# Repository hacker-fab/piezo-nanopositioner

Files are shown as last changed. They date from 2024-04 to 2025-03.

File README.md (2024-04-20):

# piezo-nanopositioner

To install the ESP-IDF you should follow this guide for [Linux and macOS](https://docs.espressif.com/projects/esp-idf/en/v5.2.1/esp32s3/get-started/linux-macos-setup.html) and [Windows](https://docs.espressif.com/projects/esp-idf/en/v5.2.1/esp32s3/get-started/windows-setup.html). Once you have the ESP-IDF installed you will need to run the `export.sh` file located in `esp/esp-idf/export.sh` inside the `esp` folder you setup. Once you have setup ESP-IDF for your current terminal session, you can now run `idf.py build` to compile the code or `idf.py -p {serial port the device is connected to} flash`.

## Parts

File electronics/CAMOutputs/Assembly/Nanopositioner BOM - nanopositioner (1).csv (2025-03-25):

Qty | Designator | MPN | Description | Value | Footprint
1 | SV2 |  | PIN HEADER |  | MA08-1
1 | SV1 |  | PIN HEADER |  | MA10-1
3 | C5, C9, C10 | GRM155R71H104KE14D | CAPACITOR, European symbol | 100n | C0402
1 | C15 | CGA3E2X7R1H104K080AA | CAPACITOR, European symbol | 100n | C0603
1 | C16 | KGM21NR71E104KT | CAPACITOR, European symbol | 100n | C0603
4 | R5, R7, R8, R9 | ERA-2AEB103X | RESISTOR, European symbol | 10k | R0402
1 | C3 | GCM155R71H103KA55D | CAPACITOR, European symbol | 10n | C0402
1 | C13 | GRM033R70J103KA01D | CAPACITOR, European symbol | 10n | C0402
1 | R1 | CRCW04021K91FKED | RESISTOR, European symbol | 1k91 | R0402
1 | C17 | EMK107B7105KA-T | CAPACITOR, European symbol | 1u | C0402
4 | C2, C6, C7, C8 | GRM155R61E105MA12D | CAPACITOR, European symbol | 1u | C0402
2 | C1, C4 | CL10A226MP8NUNE | CAPACITOR, European symbol | 22u | C0603
1 | C11 | GRM155R71A273KA01D | CAPACITOR, European symbol | 27n | C0402
1 | R13 | CRCW04022K49FKED | RESISTOR, European symbol | 2k49 | R0402
1 | C20 | GRM21BR71A225KA01L | CAPACITOR, European symbol | 2u2 | C0805
1 | L1 | SDR1307-2R7ML |  | 2u7, 8m | IND_BOURNS_SDR1307
1 | R6 | CRCW040257K6FKED | RESISTOR, European symbol | 57k6 | R0402
5 | R2, R3, R10, R11, R12 | ERA-2AEB512X | RESISTOR, European symbol | 5k1 | R0402
1 | C12 | GRM1555C1H5R6CA01D | CAPACITOR, European symbol | 5p6 | C0402
1 | J1 | 12402012E212A | WR-COM USB 2.0 Type C Plug Vertical SMT | 629722000214 | 629722000214
3 | C14, C18, C19 | C3216X5R1H685K160AB | CAPACITOR, European symbol | 6u8 | C1206
2 | R4, R14 | CRCW04029K76FKED | RESISTOR, European symbol | 9k76 | R0402
1 | D1 | B240A-13-F | Diode Schottky 40V 2A Surface Mount SMA | B240A-13-F | DIOM5226X230N
1 | U3 | DAC80504RTET |  | DAC80504RTER | RTE16_TEX
1 | U4 | ESP32-S3-WROOM-1-N4 | Check availability Check availability | ESP32-S3-WROOM-1-N4R8 | XCVR_ESP32S3WROOM1N8R8
1 | U5 | LM5157RTER |  | LM5157RTER | QFN_57RTER_TEX
1 | I1 | OPA4209AIPW |  | OPA4209AIPW | PW14
3 | TP2, TP4, TP10 |  | TEST PIN | PTR1PAD1-13 | P1-13
1 | U1 | TPS73633DBVR |  | TPS73633DBVR | DBV5
1 | U2 | USBLC6-2SC6 |  | USBLC6-2SC6 | SOT23-6L_STM

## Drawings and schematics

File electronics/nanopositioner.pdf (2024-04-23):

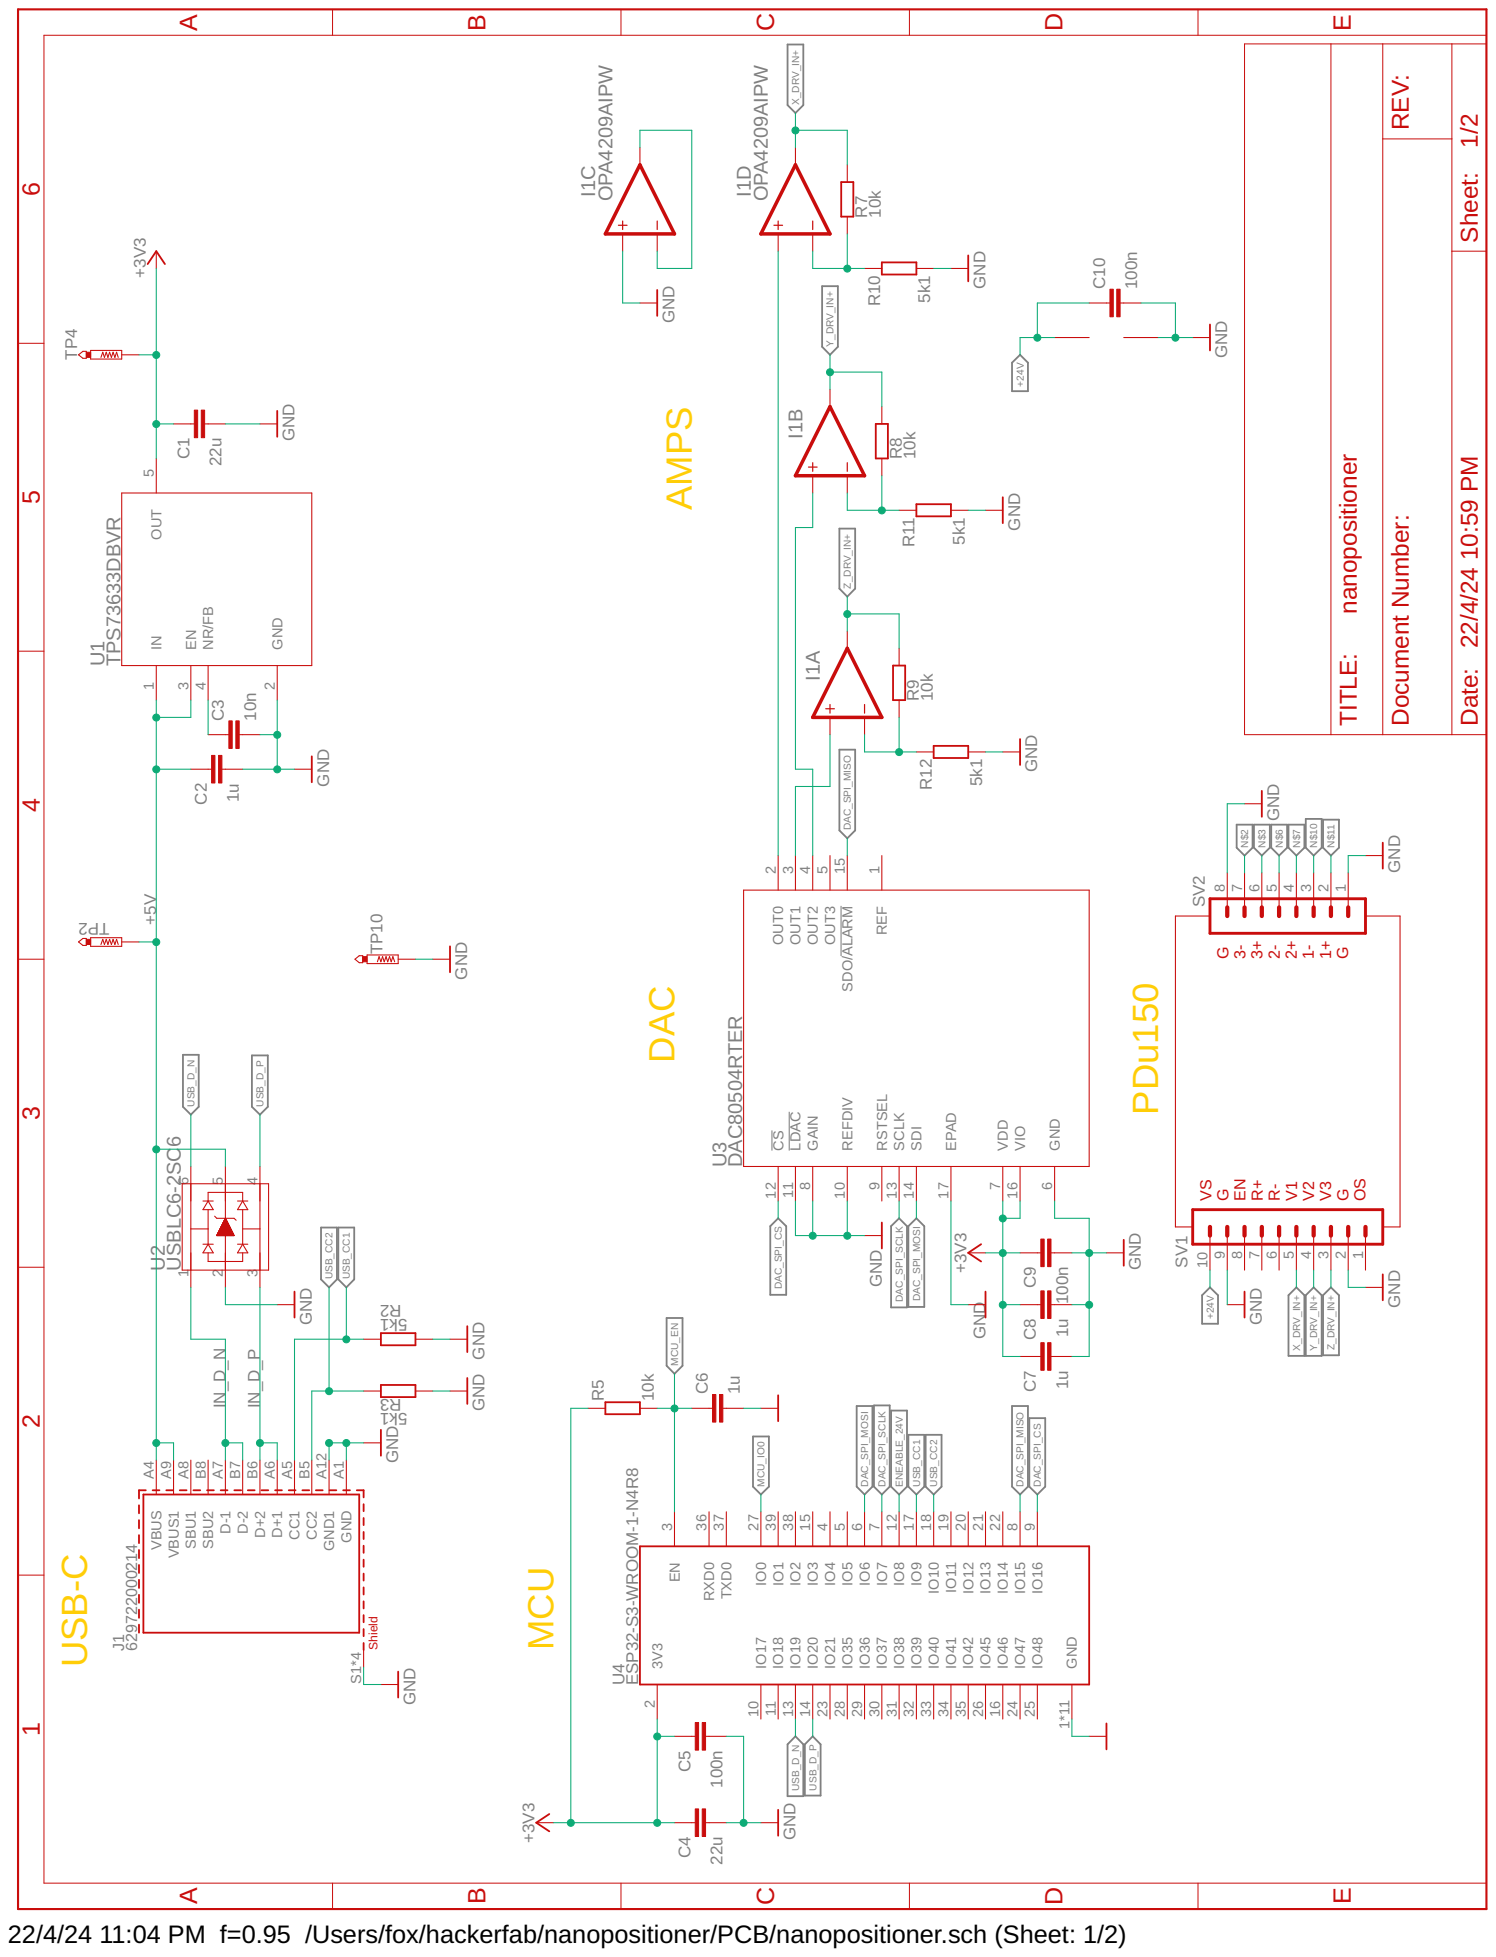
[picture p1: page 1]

GND GND

22/4/24 11:04 PM f=0.95 /Users/fox/hackerfab/nanopositioner/PCB/nanopositioner.sch (Sheet: 1/2)

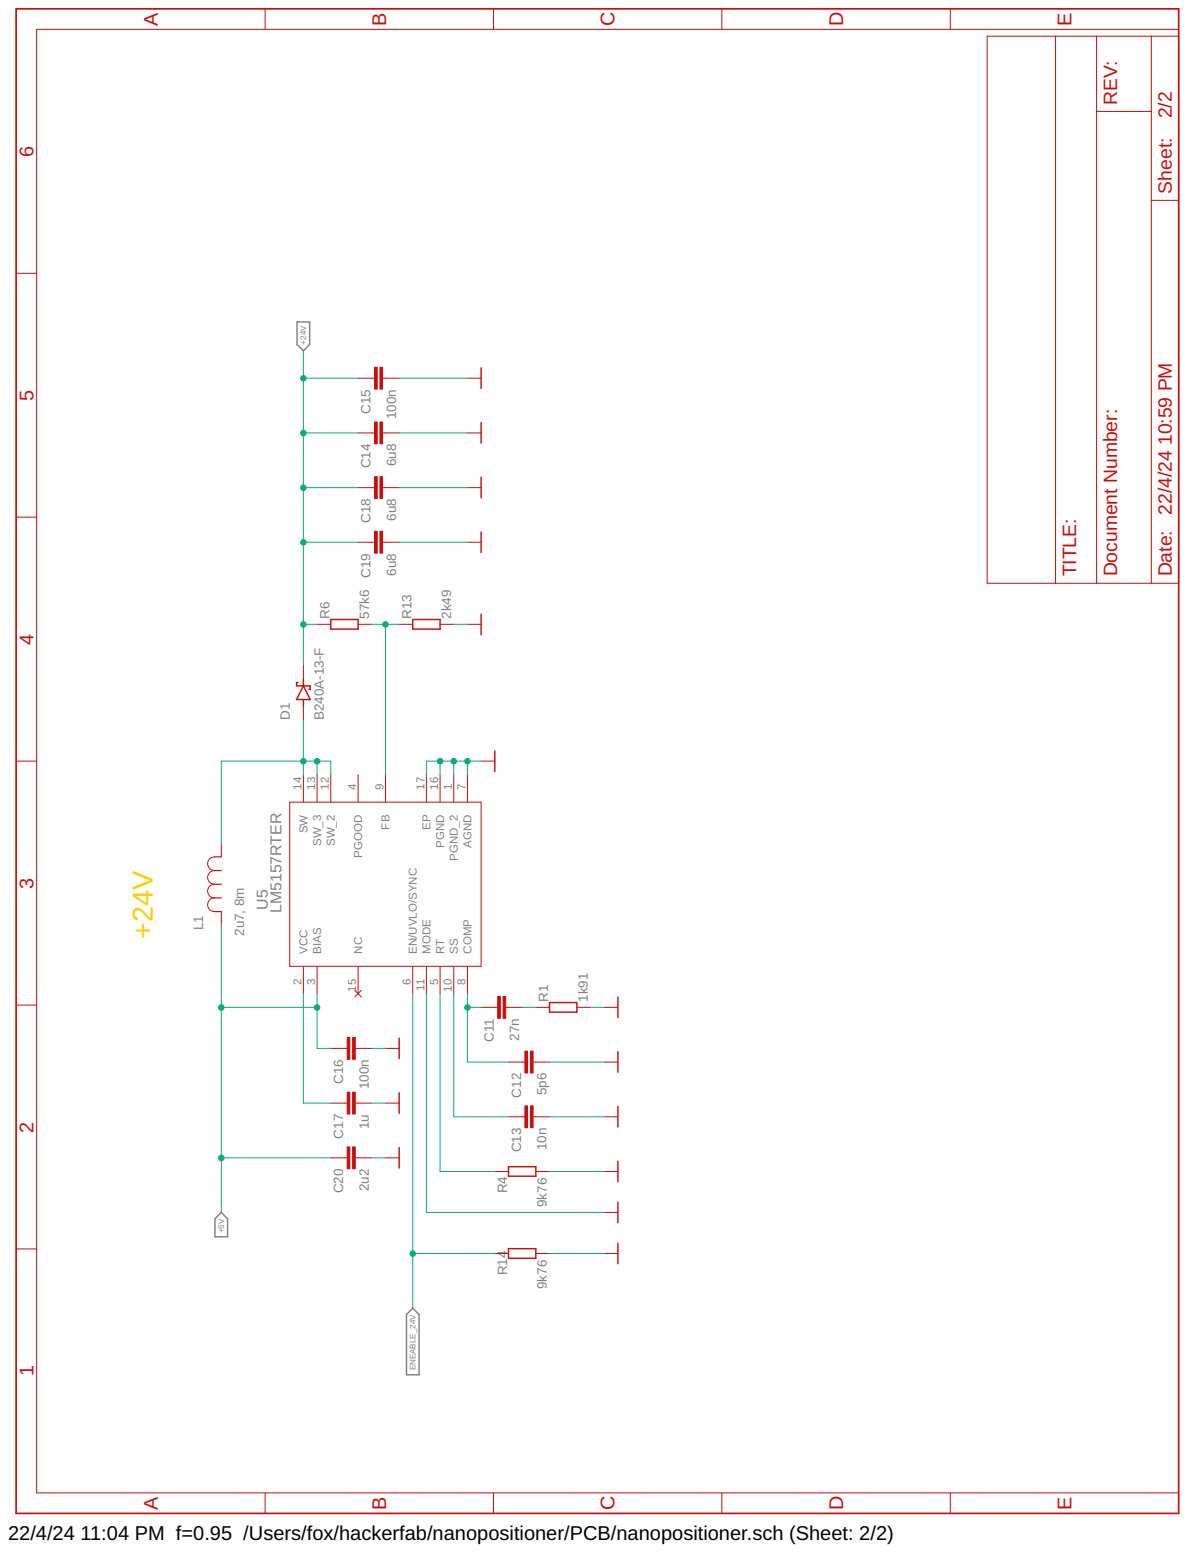
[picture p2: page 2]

22/4/24 11:04 PM f=0.95 /Users/fox/hackerfab/nanopositioner/PCB/nanopositioner.sch (Sheet: 2/2)

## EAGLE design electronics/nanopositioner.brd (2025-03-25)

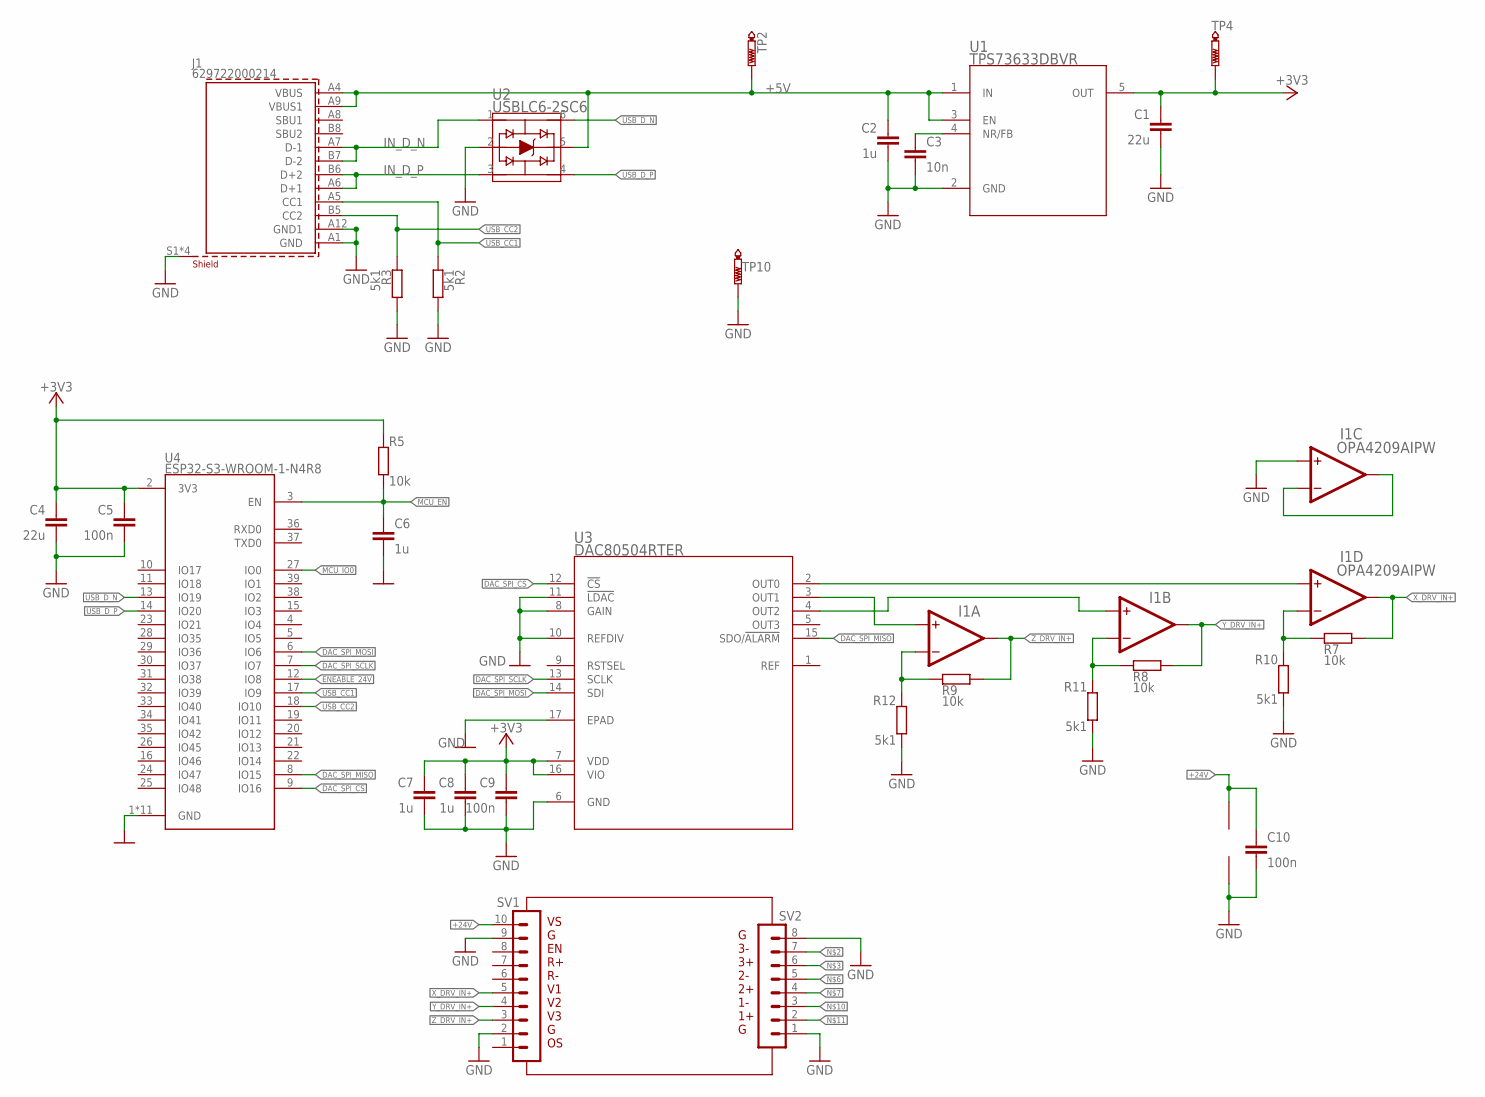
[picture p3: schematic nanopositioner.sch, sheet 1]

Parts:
C1, C4: 22u; C0603; MPN CL10A226MP8NUNE
C2, C6, C7, C8: 1u; C0402; MPN GRM155R61E105MA12D
C3: 10n; C0402; MPN GCM155R71H103KA55D
C5, C9, C10: 100n; C0402; MPN GRM155R71H104KE14D
I1: OPA4209AIPW; PW14; MPN OPA4209AIPW
J1: 629722000214; MPN 12402012E212A
R2, R3, R10, R11, R12: 5k1; R0402; MPN ERA-2AEB512X
R5, R7, R8, R9: 10k; R0402; MPN ERA-2AEB103X
SV1: MA10-1
SV2: MA08-1
TP2, TP4, TP10: PTR1PAD1-13; P1-13
U1: TPS73633DBVR; DBV5; MPN TPS73633DBVR
U2: USBLC6-2SC6; SOT23-6L_STM; MPN USBLC6-2SC6
U3: DAC80504RTER; RTE16_TEX; MPN DAC80504RTET
U4: ESP32-S3-WROOM-1-N4R8; XCVR_ESP32S3WROOM1N8R8; MPN ESP32-S3-WROOM-1-N4

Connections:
+3V3: C1.1, C4.1, C5.1, C7.1, C8.1, C9.1, R5.1, TP4.TP, U1.5 (OUT), U3.7 (VDD), U3.16 (VIO), U4.2 (3V3)
+5V: C2.2, J1.A4 (VBUS), J1.A9 (VBUS1), TP2.TP, U1.1 (IN), U1.3 (EN), U2.5; also elsewhere on the board
+24V: C10.1, I1.4, SV1.10; also elsewhere on the board
DAC_SPI_CS: U3.12 (!CS), U4.9 (IO16)
DAC_SPI_MISO: U3.15 (SDO/!ALARM), U4.8 (IO15)
DAC_SPI_MOSI: U3.14 (SDI), U4.6 (IO6)
DAC_SPI_SCLK: U3.13 (SCLK), U4.7 (IO7)
ENEABLE_24V: U4.12 (IO8); also elsewhere on the board
GND: C1.2, C2.1, C3.2, C4.2, C5.2, C6.1, C7.2, C8.2, C9.2, C10.2, I1.10 (INA+), I1.11, J1.A1 (GND), J1.A12 (GND1), J1.S1 (SHIELD), J1.S2 (SHIELD), J1.S3 (SHIELD), J1.S4 (SHIELD), R2.1, R3.2, R10.2, R11.2, R12.2, SV1.2, SV1.9, SV2.1, SV2.8, TP10.TP, U1.2 (GND), U2.2, U3.6 (GND), U3.8 (GAIN), U3.10 (REFDIV), U3.11 (!LDAC), U3.17 (EPAD), U4.1 (GND), U4.40 (GND), U4.41_1 (GND), U4.41_2 (GND), U4.41_3 (GND), U4.41_4 (GND), U4.41_5 (GND), U4.41_6 (GND), U4.41_7 (GND), U4.41_8 (GND), U4.41_9 (GND); also elsewhere on the board
IN_D_N: J1.A7 (D-1), J1.B7 (D-2), U2.1
IN_D_P: J1.A6 (D+1), J1.B6 (D+2), U2.3
MCU_EN: C6.2, R5.2, U4.3 (EN)
MCU_IO0: U4.27 (IO0)
unnamed: I1.13 (INA-), R7.1, R10.1
unnamed: C3.1, U1.4 (NR/FB)
unnamed: I1.3 (INA+), U3.3 (OUT1)
unnamed: I1.6 (INA-), R8.1, R11.1
unnamed: I1.5 (INA+), U3.4 (OUT2)
unnamed: I1.2 (INA-), R9.1, R12.1
unnamed: I1.12 (INA+), U3.2 (OUT0)
unnamed: I1.8 (OUTA), I1.9 (INA-)
USB_CC1: J1.A5 (CC1), R2.2, U4.17 (IO9)
USB_CC2: J1.B5 (CC2), R3.1, U4.18 (IO10)
USB_D_N: U2.6, U4.13 (IO19)
USB_D_P: U2.4, U4.14 (IO20)
X_DRV_IN+: I1.14 (OUTA), R7.2, SV1.5
Y_DRV_IN+: I1.7 (OUTA), R8.2, SV1.4
Z_DRV_IN+: I1.1 (OUTA), R9.2, SV1.3

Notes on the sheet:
VS G EN R+ R- V1 V2 V3 G OS
G 3- 3+ 2- 2+ 1- 1+ G

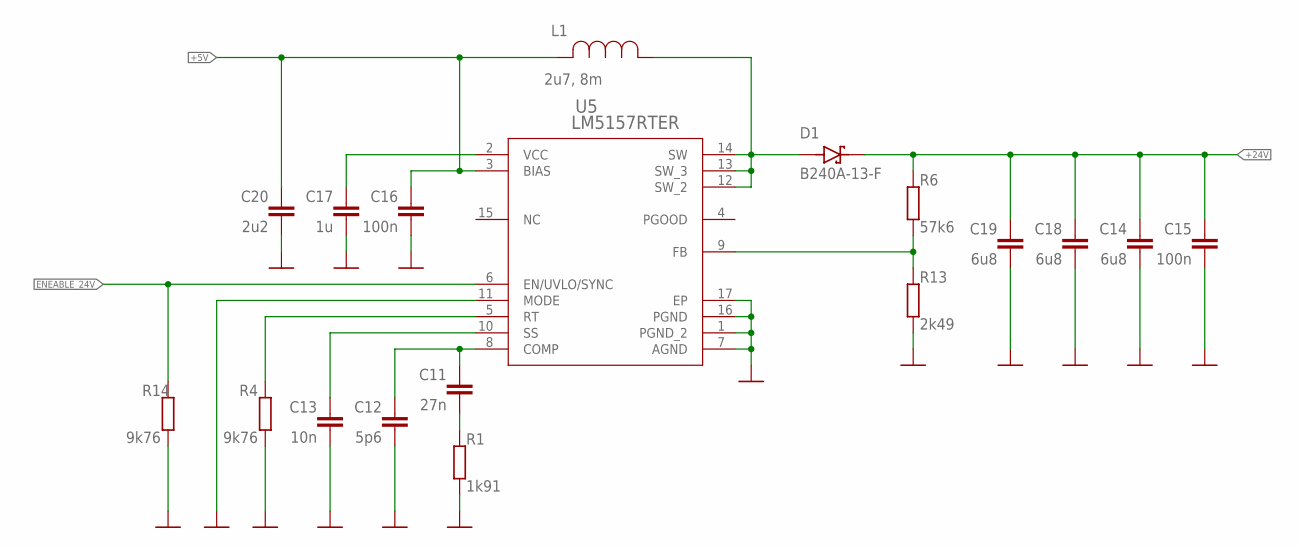
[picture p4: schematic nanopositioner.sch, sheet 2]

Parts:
C11: 27n; C0402; MPN GRM155R71A273KA01D
C12: 5p6; C0402; MPN GRM1555C1H5R6CA01D
C13: 10n; C0402; MPN GRM033R70J103KA01D
C14, C18, C19: 6u8; C1206; MPN C3216X5R1H685K160AB
C15: 100n; C0603; MPN CGA3E2X7R1H104K080AA
C16: 100n; C0603; MPN KGM21NR71E104KT
C17: 1u; C0402; MPN EMK107B7105KA-T
C20: 2u2; C0805; MPN GRM21BR71A225KA01L
D1: B240A-13-F; DIOM5226X230N; MPN B240A-13-F
L1: 2u7, 8m; IND_BOURNS_SDR1307; MPN SDR1307-2R7ML
R1: 1k91; R0402; MPN CRCW04021K91FKED
R4, R14: 9k76; R0402; MPN CRCW04029K76FKED
R6: 57k6; R0402; MPN CRCW040257K6FKED
R13: 2k49; R0402; MPN CRCW04022K49FKED
U5: LM5157RTER; QFN_57RTER_TEX; MPN LM5157RTER

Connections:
+5V: C16.2, C20.2, L1.2, U5.3 (BIAS); also elsewhere on the board
+24V: C14.2, C15.2, C18.2, C19.2, D1.C (K), R6.1; also elsewhere on the board
ENEABLE_24V: R14.1, U5.6 (EN/UVLO/SYNC); also elsewhere on the board
GND: C12.1, C13.1, C14.1, C15.1, C16.1, C17.1, C18.1, C19.1, C20.1, R1.2, R4.2, R13.2, R14.2, U5.1 (PGND_2), U5.7 (AGND), U5.11 (MODE), U5.16 (PGND), U5.17 (EP); also elsewhere on the board
unnamed: C11.2, C12.2, U5.8 (COMP)
unnamed: C11.1, R1.1
unnamed: C13.2, U5.10 (SS)
unnamed: R4.1, U5.5 (RT)
unnamed: D1.A, L1.1, U5.12 (SW_2), U5.13 (SW_3), U5.14 (SW)
unnamed: R6.2, R13.1, U5.9 (FB)
unnamed: C17.2, U5.2 (VCC)
PGOOD: U5.4 (PGOOD)

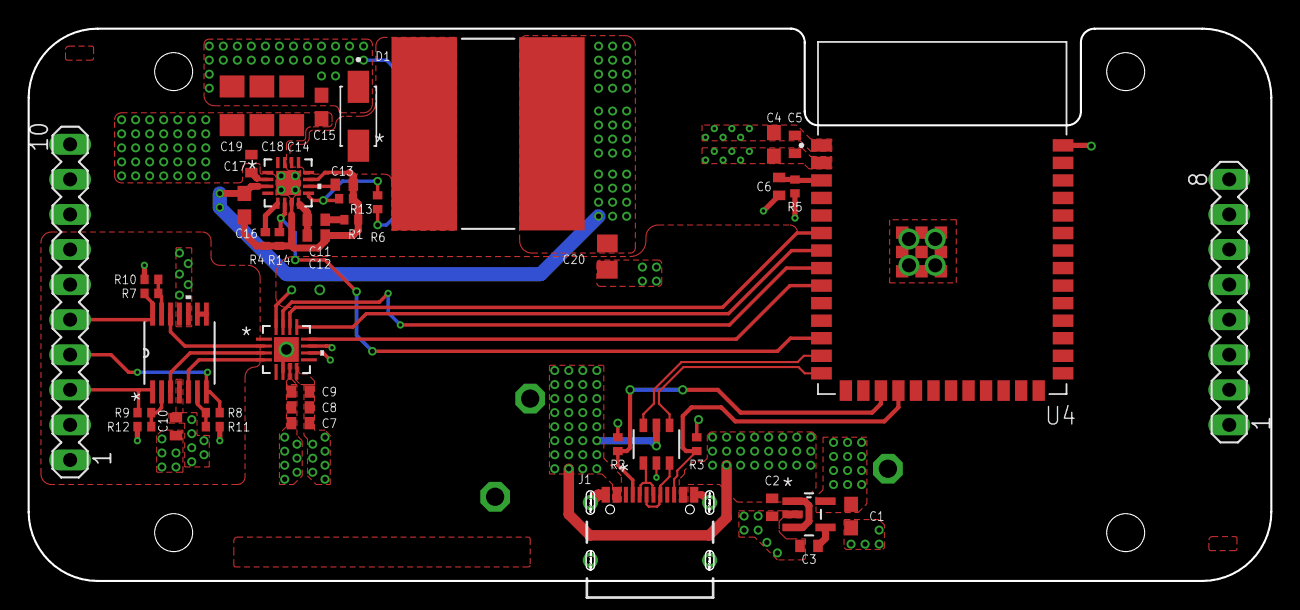
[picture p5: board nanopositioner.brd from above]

Board: 4 copper layers, 90.0 x 40.0 mm, 48 parts (0 on the bottom side), 34 nets.

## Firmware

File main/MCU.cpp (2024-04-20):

#include "driver/spi_common.h"
#include "driver/spi_master.h"
#include "driver/uart.h"
#include "esp_err.h"
#include "esp_system.h"
#include "freertos/FreeRTOS.h"
#include "freertos/portmacro.h"
#include "freertos/task.h"
#include "driver/gpio.h"
#include "hal/gpio_types.h"
#include <stdint.h>
#include <sys/_stdint.h>
#include <sys/errno.h>
#include <sys/types.h>
#include <string.h>
#include <math.h>
#include <string>
#include "esp_timer.h"
#include "hal/usb_phy_types.h"
#include "tinyusb.h"
#include "tusb_cdc_acm.h"
#include "tusb_console.h"

const gpio_num_t ENEABLE_24V_PIN = GPIO_NUM_8;
const gpio_num_t DAC_SPI_MOSI = GPIO_NUM_6;
const gpio_num_t DAC_SPI_MISO = GPIO_NUM_15;
const gpio_num_t DAC_SPI_SCLK = GPIO_NUM_7;
const gpio_num_t DAC_SPI_CS = GPIO_NUM_16;

const int railCorrection = 12000;
const int maxADCValue = pow(2, 16)-1-railCorrection;

int g_itf;
int driveFrequency = 1000;
uint8_t transactionBuffer[CONFIG_TINYUSB_CDC_RX_BUFSIZE + 1] = {0};

int isDriverOn = 0;
int safeToRun = 1;
int running = 0;
spi_device_handle_t SPIDevice;

enum DACRegister : uint8_t {
	NOP = 0x00,
	DEVICEID = 0x01,
	SYNC = 0x02,
	CONFIG = 0x02,
	GAIN = 0x04,
	TRIGGER = 0x05,
	BRDCAST = 0x06,
	STATUS = 0x07,
	DAC0VAl = 0x08,
	DAC1VAl = 0x09,
	DAC2VAL = 0x0A,
	DAC3VAL = 0x0B,
};

enum DACChannel : uint8_t {
	DAC0 = 0,
	DAC1 = 1,
	DAC2 = 2,
	DAC3 = 3,
};

enum USBOpCode : uint32_t {
	ABORT = 0x74726261, // abrt
	RUN = 0x706E7572, // runp
	SETCH = 0x63746573, // setc
	SETFREQ = 0x66746573, // setf
};

void turnDriver(uint32_t on) {
	gpio_set_level(ENEABLE_24V_PIN, on);
}

void setupPins() {
	gpio_set_direction(ENEABLE_24V_PIN, GPIO_MODE_OUTPUT);
}

void initiateSPI(){

	spi_bus_config_t buscfg = {
		.mosi_io_num = DAC_SPI_MOSI,
		.miso_io_num = DAC_SPI_MISO,
		.sclk_io_num = DAC_SPI_SCLK,
		.max_transfer_sz = 4092,
	};

	spi_device_interface_config_t devcfg = {
		.command_bits = 0,
		.address_bits = 0,
		.dummy_bits = 0,
		.mode = 1,
		.clock_source = SPI_CLK_SRC_DEFAULT,
		.cs_ena_pretrans = 0,
		.cs_ena_posttrans = 0,
		.clock_speed_hz = SPI_MASTER_FREQ_40M,
		.spics_io_num = DAC_SPI_CS,
		.queue_size = 7,
	};

	esp_err_t ret;

	ret = spi_bus_initialize(SPI2_HOST, &buscfg, SPI_DMA_DISABLED);
	assert(ret==ESP_OK);

	ret = spi_bus_add_device(SPI2_HOST, &devcfg, &SPIDevice);
	assert(ret==ESP_OK);

	vTaskDelay(100 / portTICK_PERIOD_MS);
}

void writeToRegister(DACRegister address, uint16_t value)    {
	spi_device_acquire_bus(SPIDevice, portMAX_DELAY);
	spi_transaction_t transaction = {
		.flags = SPI_TRANS_USE_TXDATA,
		.length = 3*8,
	};

	transaction.tx_data[0] = (0b00000000 + (uint8_t)address);
	transaction.tx_data[1] = value >> 8;
	transaction.tx_data[2] = value;

	esp_err_t ret;
	ret = spi_device_transmit(SPIDevice, &transaction);
	assert(ret==ESP_OK);
	spi_device_release_bus(SPIDevice);
}

void fast_writeToRegister(DACRegister address, uint16_t value)    {
	spi_transaction_t transaction = {
		.flags = SPI_TRANS_USE_TXDATA,
		.length = 3*8,
	};

	transaction.tx_data[0] = (0b00000000 + (uint8_t)address);
	transaction.tx_data[1] = value >> 8;
	transaction.tx_data[2] = value;

	spi_device_polling_transmit(SPIDevice, &transaction);
}

void readFromRegister(DACRegister address, uint16_t &value){
	spi_device_acquire_bus(SPIDevice, portMAX_DELAY);
	uint8_t t_bytes[3];
	t_bytes[0] = (0b10000000 + (uint8_t)address);
	t_bytes[1] = 0;
	t_bytes[2] = 0;

	uint8_t r_bytes[3];
	memset(r_bytes, 0, sizeof(r_bytes));

	spi_transaction_t transaction = {
		.length = sizeof(t_bytes)*8,    // length in bits
		.tx_buffer = t_bytes,
		.rx_buffer = r_bytes
	};

	esp_err_t ret;
	ret = spi_device_transmit(SPIDevice, &transaction);
	assert(ret==ESP_OK);

	memset(r_bytes, 0, sizeof(r_bytes));

	transaction = {
		.length = sizeof(r_bytes)*8,    // length in bits
		.tx_buffer = r_bytes,
		.rx_buffer = r_bytes
	};

	ret = spi_device_transmit(SPIDevice, &transaction);
	assert(ret==ESP_OK);

	value = (uint16_t)(r_bytes[1] << 8 | r_bytes[2]);
	spi_device_release_bus(SPIDevice);
}

void setChannelBroadcast(DACChannel channel, int broadcast) {
	uint16_t registerValue = 0;
	readFromRegister(DACRegister::SYNC, registerValue);

	if(broadcast)
		writeToRegister(DACRegister::SYNC, registerValue | (1 << (8+channel)));
	else
		writeToRegister(DACRegister::SYNC, registerValue & (1 << (8+channel)));
}

void broadcast(uint16_t value) {
	writeToRegister(DACRegister::BRDCAST, value);
}

void fast_broadcast(uint16_t value) {
	fast_writeToRegister(DACRegister::BRDCAST, value+railCorrection);
}

long map(long x, long in_min, long in_max, long out_min, long out_max) {
    return (x - in_min) * (out_max - out_min) / (in_max - in_min) + out_min;
}

void stickSlip(int frequency, int direction) {
  long usPeriod = 1000000 / frequency;
  uint64_t usStart = esp_timer_get_time();
	uint64_t now = esp_timer_get_time();

	fast_broadcast(direction ? 0 : maxADCValue);

  while (1) {
		now = esp_timer_get_time();
		if (now - usStart > usPeriod) break;
		if (!safeToRun) return;

		if (direction == 1) {
			fast_broadcast((double)maxADCValue * pow((double)(now - usStart) / (double)usPeriod, 2));
		} else {
			fast_broadcast(maxADCValue - (double)maxADCValue * pow((double)(now - usStart) / (double)usPeriod, 2));
		}
	}

	fast_broadcast(0);
}

void initiateDAC() {
	setChannelBroadcast(DACChannel::DAC0, 0);
	setChannelBroadcast(DACChannel::DAC1, 0);
	setChannelBroadcast(DACChannel::DAC2, 0);
	setChannelBroadcast(DACChannel::DAC3, 0);

	writeToRegister(DACRegister::GAIN, 0b0000000100001111);
}

bool startsWithOpcode(int msgSize, USBOpCode opCode) {
	if(msgSize<sizeof(opCode))
		return 0;
	
	return memcmp(transactionBuffer, &opCode, sizeof(opCode)) == 0;
}

bool bufferContentIsBool(int i) {
	if(transactionBuffer[i]<48 || transactionBuffer[i]>48+1) return 0;
	
	return 1;
}

bool bufferContentIsNumber(int i) {
	if(transactionBuffer[i]<48 || transactionBuffer[i]>57) return 0;
	
	return 1;
}

void USBHandler(int msgSize) {
	if(startsWithOpcode(msgSize, USBOpCode::ABORT)) {
		safeToRun=0;
		running=0;

		tinyusb_cdcacm_write_queue((tinyusb_cdcacm_itf_t)g_itf, transactionBuffer, 4);
		tinyusb_cdcacm_write_flush((tinyusb_cdcacm_itf_t)g_itf, 0);

		return;
	}

	if(running) return;
	safeToRun=1;

	if(startsWithOpcode(msgSize, USBOpCode::SETCH)) {
		if(msgSize<7) return;

		for(int i=0; i<3; i++) {
			if(!bufferContentIsBool(4+i)) return;
		}

		setChannelBroadcast(DACChannel::DAC0, transactionBuffer[4]-48);
		setChannelBroadcast(DACChannel::DAC1, transactionBuffer[5]-48);
		setChannelBroadcast(DACChannel::DAC2, transactionBuffer[6]-48);

		tinyusb_cdcacm_write_queue((tinyusb_cdcacm_itf_t)g_itf, transactionBuffer, 4);
		tinyusb_cdcacm_write_flush((tinyusb_cdcacm_itf_t)g_itf, 0);

		return;
	}

	if(startsWithOpcode(msgSize, USBOpCode::SETFREQ)) {
		if(msgSize<9) return;

		for(int i=0; i<5; i++) {
			if(!bufferContentIsNumber(4+i)) return;
		}
		std::string n(transactionBuffer+4, transactionBuffer+4+5);
		driveFrequency = std::stoi(n);

		tinyusb_cdcacm_write_queue((tinyusb_cdcacm_itf_t)g_itf, transactionBuffer, 4);
		tinyusb_cdcacm_write_flush((tinyusb_cdcacm_itf_t)g_itf, 0);

		return;
	}

	if(startsWithOpcode(msgSize, USBOpCode::RUN)) {
		if(msgSize<7) return;

		if(!bufferContentIsBool(4)) return;

		for(int i=0; i<2; i++) {
			if(!bufferContentIsNumber(4+i)) return;
		}

		running=1;

		std::string n(transactionBuffer+5, transactionBuffer+5+2);
		int usDuration = std::stoi(n) * 1000000;

		spi_device_acquire_bus(SPIDevice, portMAX_DELAY);

		uint64_t yieldTimer = esp_timer_get_time();
		uint64_t usStart = yieldTimer;
		while(esp_timer_get_time() - usStart < usDuration) {
			if (esp_timer_get_time() - yieldTimer > 10000000) {
				vPortYield(); // yield
				yieldTimer = esp_timer_get_time();
			}

			if(!safeToRun) {
				safeToRun=1;
				return;
			}

			stickSlip(driveFrequency, transactionBuffer[4]-48);
		}
		spi_device_release_bus(SPIDevice);

		running=0;

		tinyusb_cdcacm_write_queue((tinyusb_cdcacm_itf_t)g_itf, transactionBuffer, 4);
		tinyusb_cdcacm_write_flush((tinyusb_cdcacm_itf_t)g_itf, 0);

		return;
	}

}

void tinyusb_cdc_rx_callback(int itf, cdcacm_event_t *event) {
	size_t rx_size = 0;

	tinyusb_cdcacm_read((tinyusb_cdcacm_itf_t)itf, transactionBuffer, CONFIG_TINYUSB_CDC_RX_BUFSIZE, &rx_size);
	if(rx_size > 0){
		g_itf = itf;

		USBHandler(rx_size);
	}
}

void initiateUSB() {
		const tinyusb_config_t tusb_cfg = {
		.device_descriptor = NULL,
		.string_descriptor = NULL,
		.external_phy = false,
		.configuration_descriptor = NULL,
	};

	ESP_ERROR_CHECK(tinyusb_driver_install(&tusb_cfg));

	tinyusb_config_cdcacm_t acm_cfg;
	memset(&acm_cfg, 0, sizeof(acm_cfg));
	acm_cfg.callback_rx = &tinyusb_cdc_rx_callback;

	ESP_ERROR_CHECK(tusb_cdc_acm_init(&acm_cfg));

	esp_tusb_init_console(TINYUSB_CDC_ACM_0);
}

extern "C" void app_main(void) {
	setupPins();
	turnDriver(1);
	
	initiateSPI();
	initiateDAC();
	initiateUSB();
}

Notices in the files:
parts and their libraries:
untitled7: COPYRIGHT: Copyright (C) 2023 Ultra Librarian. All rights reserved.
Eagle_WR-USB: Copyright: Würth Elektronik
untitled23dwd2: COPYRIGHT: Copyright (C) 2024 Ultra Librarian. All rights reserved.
